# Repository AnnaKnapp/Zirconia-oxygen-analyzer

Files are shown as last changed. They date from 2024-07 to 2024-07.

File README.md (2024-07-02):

This repository contains the hardware design files and software for a high precision oxygen analyzer.

Analyzer hardware description:
The analyzer uses a fast-response dual-cell zirconia oxygen sensor manufactured by Process Sensing Technologies. A thermocouple probe is fitted into the sensor to enable a PID controller to hold the sensing element at a constant temperature. An analog feedback loop based on the one described by Benammar and Maskell (Benamar, 1993) holds the average O2 partial pressure inside the sealed central chamber of the sensor at a fixed ratio with that of the external sample gas. A 16-bit digital-to-analog-converter (DAC) is used to generate a 1 Hz sinusoidal waveform to pump oxygen into and out of the central chamber using the pumping cell. The digital pumping signal is controlled by a custom-built digital lock-in amplifier. The Nernst potential generated across the sensing cell is digitized with a 32-bit analog-to-digital converter. The amplitude and phase of the sense signal is calculated by the lock-in amplifier and a 10-second moving average filter is applied.

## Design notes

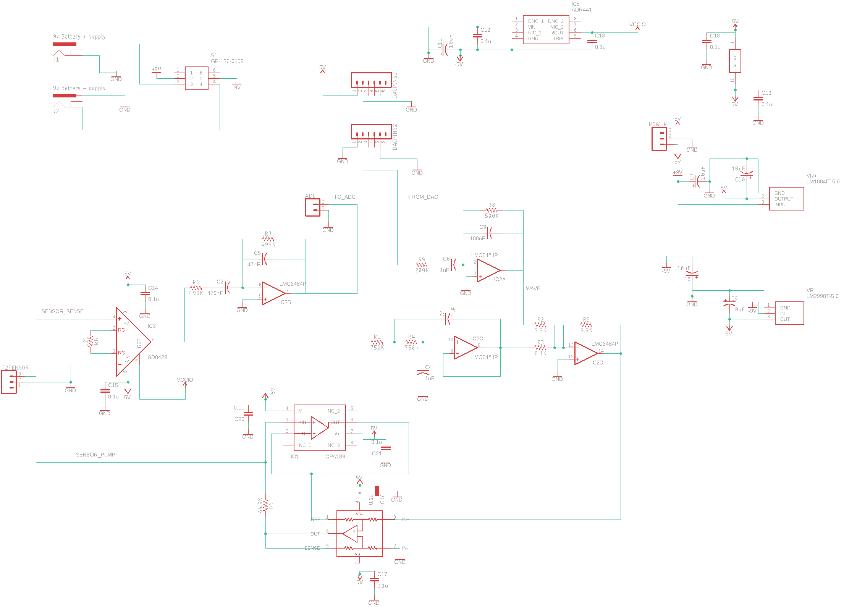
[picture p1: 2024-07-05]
Hardware/O2-analyzer-tracking-mode-schematic.png

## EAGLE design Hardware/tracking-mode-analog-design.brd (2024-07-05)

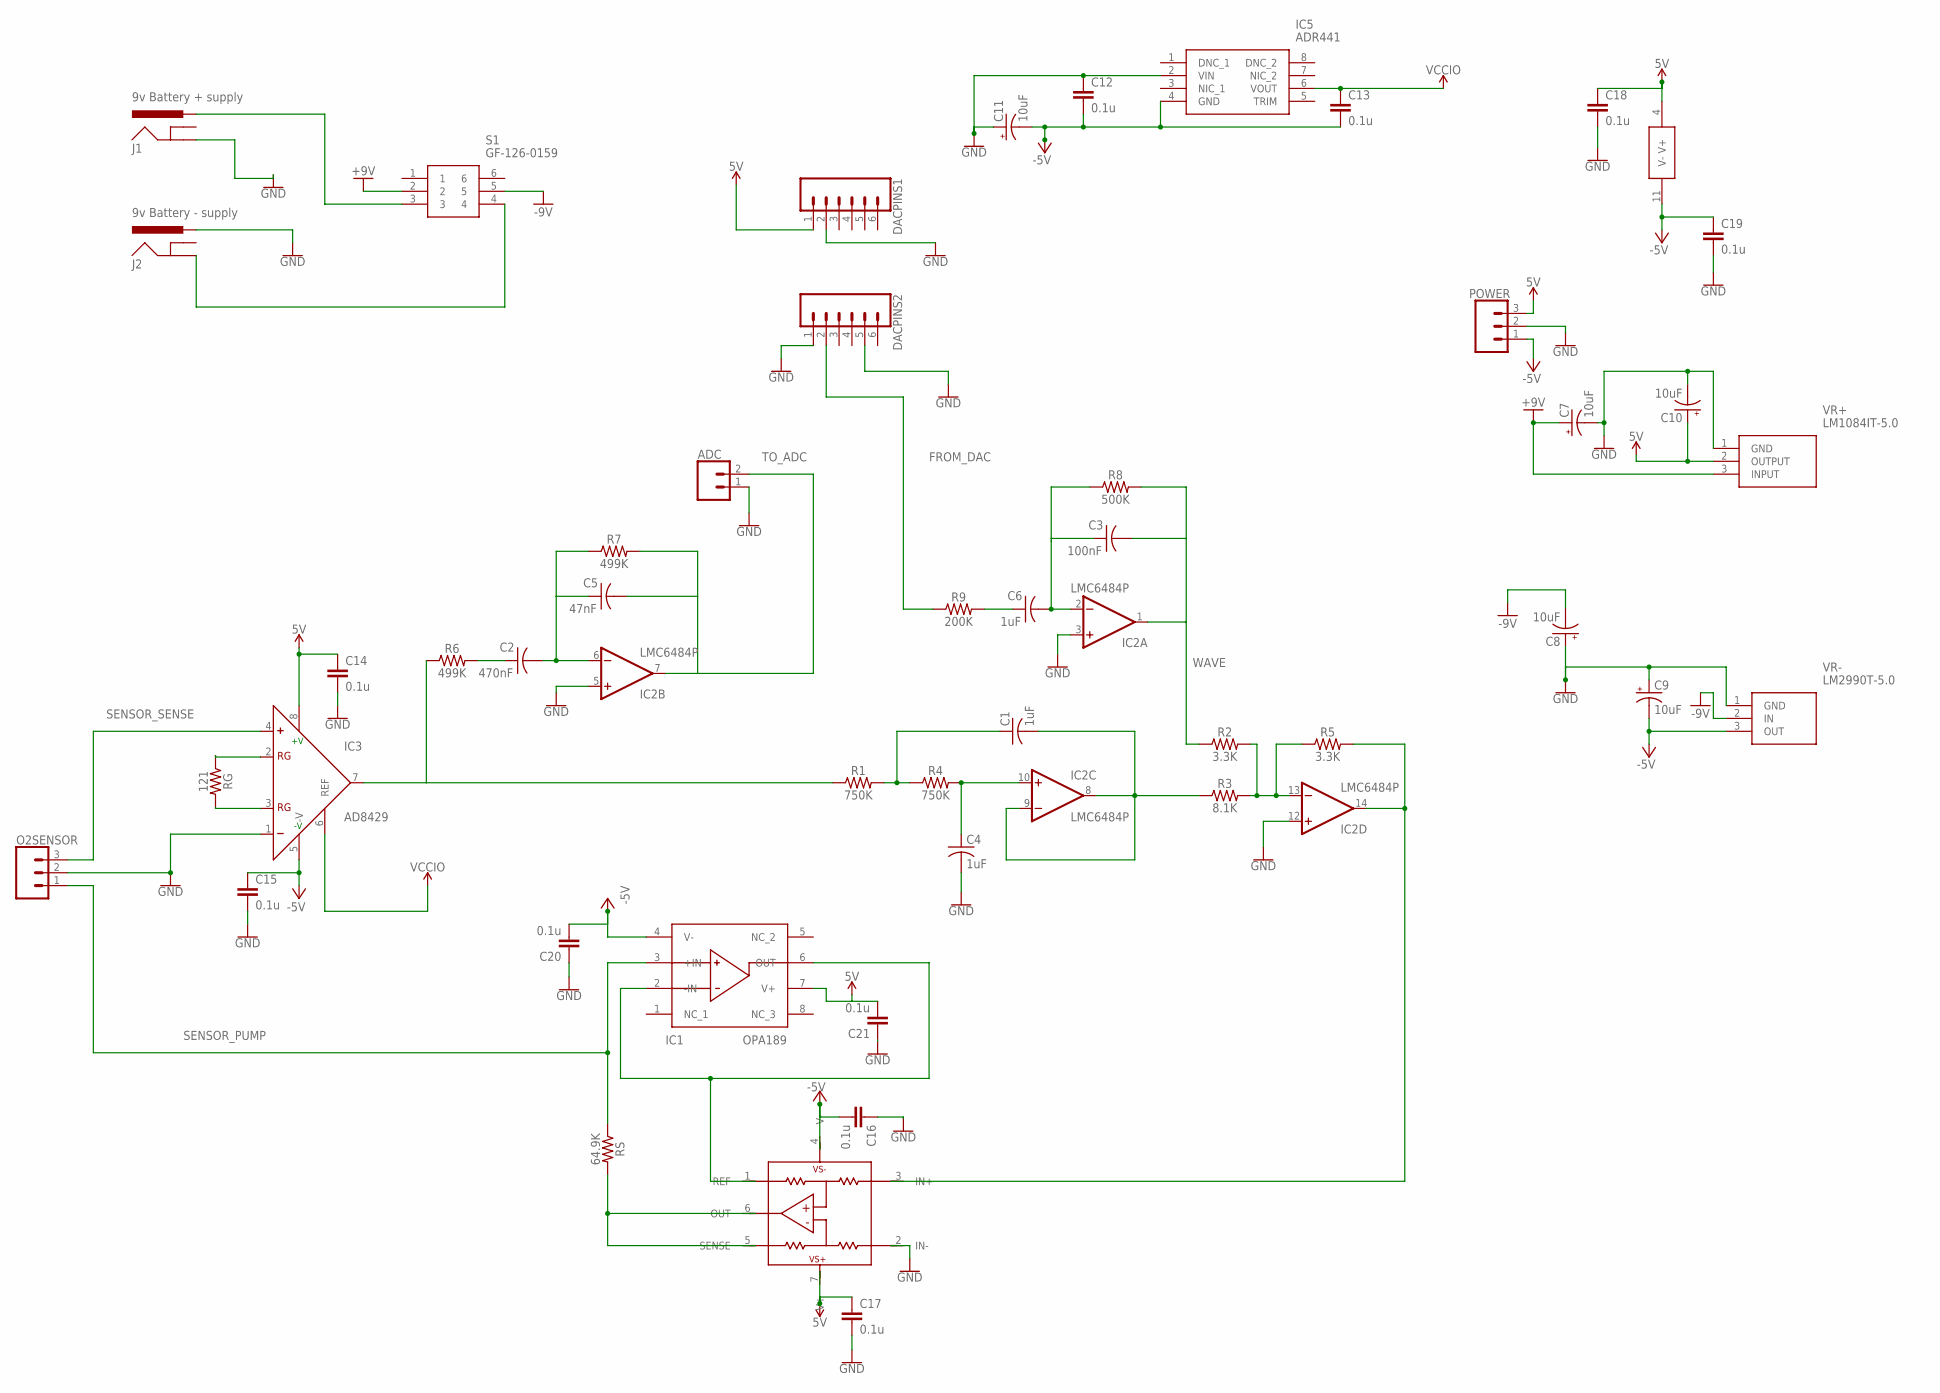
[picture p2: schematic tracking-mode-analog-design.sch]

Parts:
ADC: CONN_02; 1X02
C1, C4, C6: 1uF; C025-030X050
C2: 470nF; C025-030X050
C3: 100nF; C025-030X050
C5: 47nF; C025-030X050
C7, C8, C9, C10, C11: 10uF; CPOL-RADIAL-2.5MM-5MM-KIT
C12, C13, C14, C15, C16, C17, C18, C19, C20, C21: 0.1u; C025-040X050
DACPINS1, DACPINS2: CONN_06SILK_FEMALE_PTH; 1X06
IC1: OPA189; SOIC127P600X175-8N
IC2: LMC6484P; DIL14
IC3: AD8429; SO8
IC5: ADR441; SOIC127P600X175-8N
INA592: INA592; SO08
J1: 9v Battery + supply; POWER_JACK_PTH_BREAD
J2: 9v Battery - supply; POWER_JACK_PTH_BREAD
O2SENSOR: CONN_03; 1X03
POWER: CONN_03; 1X03
R1, R4: 750K; AXIAL-0.3
R2, R5: 3.3K; AXIAL-0.3
R3: 8.1K; AXIAL-0.3
R6, R7: 499K; AXIAL-0.3
R8: 500K; AXIAL-0.3
R9: 200K; AXIAL-0.3
RG: 121; AXIAL-0.3
RS: 64.9K; AXIAL-0.3
S1: GF-126-0159; GF1260159
VR+: LM1084IT-5.0; TO254P470X1028X1955-3P
VR-: LM2990T-5.0; TO254P470X1028X1955-3P

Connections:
5V: C10.1 (+), C14.1, C17.1, C18.1, C21.2, DACPINS1.1, IC1.7 (V+), IC2.4 (V+), IC3.8 (+V), INA592.7 (V+), POWER.3, VR+.2 (OUTPUT)
+V: C7.1 (+), S1.2, VR+.3 (INPUT)
-5V: C9.2 (-), C11.2 (-), C12.2, C13.2, C15.1, C16.2, C19.1, C20.2, IC1.4 (V-), IC2.11 (V-), IC3.5 (-V), IC5.4 (GND), INA592.4 (V-), POWER.1, VR-.3 (OUT)
-V: C8.2 (-), S1.5, VR-.2 (IN)
FROM_DAC: DACPINS2.2, R9.P$1 (1)
GND: ADC.1, C4.2, C7.2 (-), C8.1 (+), C9.1 (+), C10.2 (-), C11.1 (+), C12.1, C14.2, C15.2, C16.1, C17.2, C18.2, C19.2, C20.1, C21.1, DACPINS1.2, DACPINS2.1, DACPINS2.5, IC2.3 (+IN), IC2.5 (+IN), IC2.12 (+IN), IC3.1 (-), IC5.2 (VIN), INA592.2 (IN-), J1.GND, J2.PWR, O2SENSOR.2, POWER.2, VR+.1 (GND), VR-.1 (GND)
unnamed: C2.2, C5.1, IC2.6 (-IN), R7.P$1 (1)
unnamed: INA592.5 (SENSE), INA592.6 (OUT), RS.P$2 (2)
unnamed: C2.1, R6.P$2 (2)
unnamed: IC3.7 (OUT), R1.P$1 (1), R6.P$1 (1)
unnamed: C1.1, R1.P$2 (2), R4.P$1 (1)
unnamed: C4.1, IC2.10 (+IN), R4.P$2 (2)
unnamed: C1.2, IC2.8 (OUT), IC2.9 (-IN), R3.P$1 (1)
unnamed: IC2.13 (-IN), R2.P$2 (2), R3.P$2 (2), R5.P$1 (1)
unnamed: IC1.2 (-IN), IC1.6 (OUT), INA592.1 (REF)
unnamed: IC2.14 (OUT), INA592.3 (IN+), R5.P$2 (2)
unnamed: C6.1, R9.P$2 (2)
unnamed: IC3.2 (RG), RG.P$1 (1)
unnamed: C3.1, C6.2, IC2.2 (-IN), R8.P$1 (1)
unnamed: J2.GND, S1.4
unnamed: J1.PWR, S1.3
unnamed: IC3.3 (RG), RG.P$2 (2)
SENSOR_PUMP: IC1.3 (+IN), O2SENSOR.1, RS.P$1 (1)
SENSOR_SENSE: IC3.4 (+), O2SENSOR.3
TO_ADC: ADC.2, C5.2, IC2.7 (OUT), R7.P$2 (2)
VCCIO: C13.1, IC3.6 (REF), IC5.6 (VOUT)
WAVE: C3.2, IC2.1 (OUT), R2.P$1 (1), R8.P$2 (2)

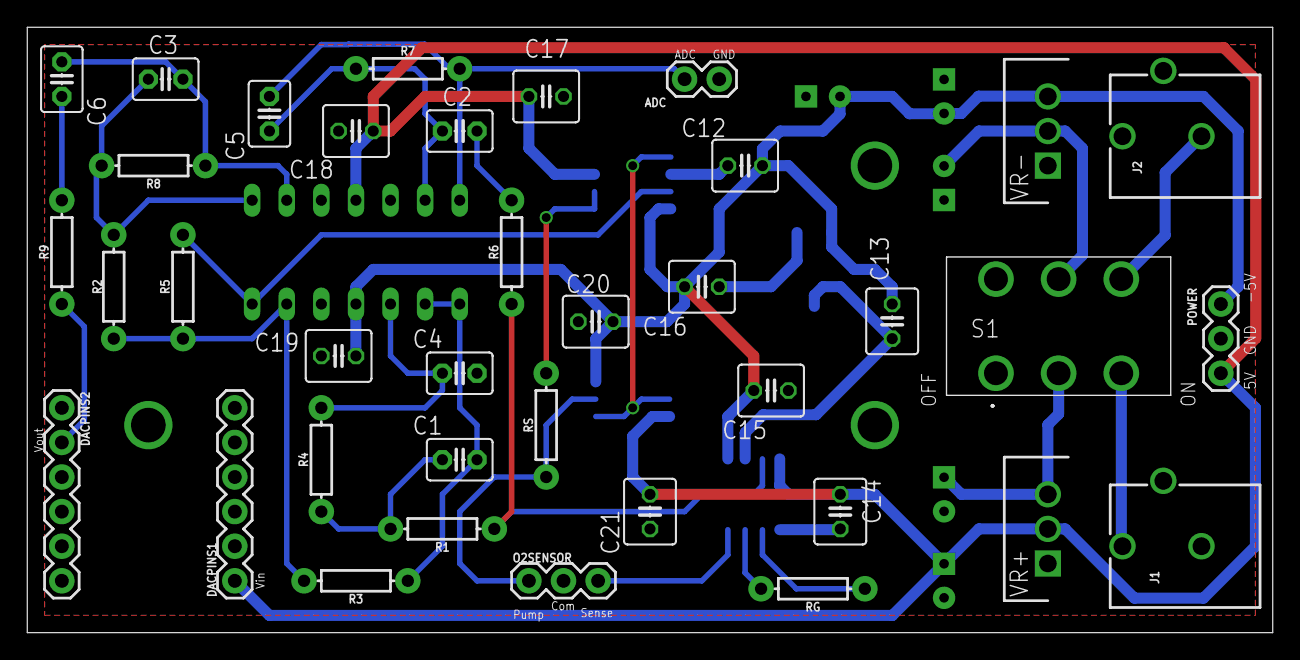
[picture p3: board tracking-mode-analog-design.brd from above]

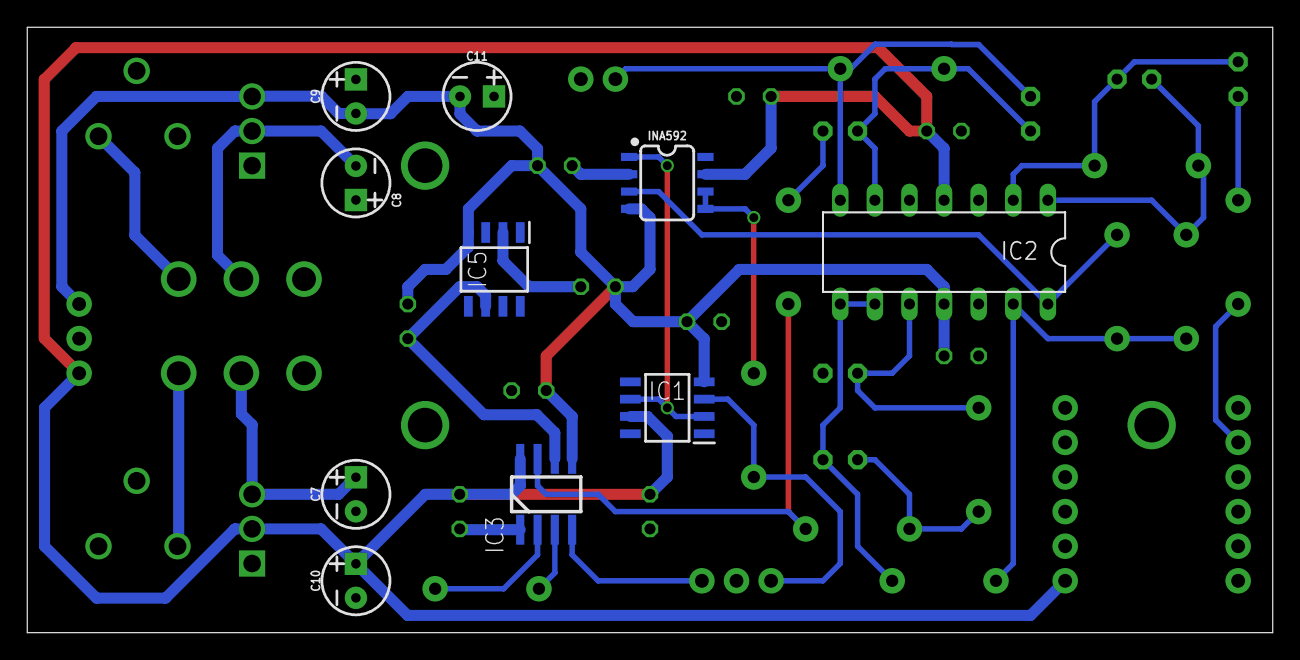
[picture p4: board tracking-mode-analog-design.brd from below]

Board: 2 copper layers, 91.4 x 44.5 mm, 47 parts (10 on the bottom side), 27 nets.

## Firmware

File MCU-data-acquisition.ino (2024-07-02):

// the ADC communicates using SPI, so include the library:
#include <SPI.h>
#include "Adafruit_AD569x.h"

#include <SPI.h>
#include "wiring_private.h" // pinPeripheral() function
//mosi on 16, miso on 7, sck on 17  

Adafruit_AD569x ad5693;
SPIClass mySPI (&sercom1, 7, 17, 16, SPI_PAD_0_SCK_1, SERCOM_RX_PAD_3);

const byte RREG = 0x20;     // ADS1262/3 read reg command
const byte WREG = 0x40;   // ADS1262/3 write reg command
const byte POWER_ADDRESS = 0x01;

const byte readcommand = 0x12;

// pins used for the connection with the sensor
// the other you need are controlled by the SPI library):
const int dataReadyPin = 3;
const int startpin = 4;
const int pwdnpin = 5;

const int dataReadyPin_2 = 26;
const int startpin_2 = 28;
const int pwdnpin_2 = 30;

byte dataToSend[8];

int i = 0;

// Generally, you should use "unsigned long" for variables that hold time
// The value will quickly become too large for an int to store
unsigned long previousMicros = 0;        // will store last time LED was updated

// constants won't change:
const long interval = 2000;
const int dac =  A0;
const PROGMEM unsigned int sine[] = {0x7F58,0x80EF,0x8286,0x841D,0x85B4,0x874A,0x88E1,
0x8A76,0x8C0C,0x8DA1,0x8F35,0x90C8,0x925B,0x93ED,
0x957F,0x970F,0x989F,0x9A2D,0x9BBA,0x9D47,0x9ED2,
0xA05B,0xA1E4,0xA36B,0xA4F0,0xA674,0xA7F7,0xA977,
0xAAF6,0xAC74,0xADEF,0xAF69,0xB0E1,0xB256,0xB3CA,
0xB53B,0xB6AB,0xB818,0xB982,0xBAEB,0xBC51,0xBDB4,
0xBF15,0xC074,0xC1D0,0xC329,0xC47F,0xC5D3,0xC724,
0xC871,0xC9BC,0xCB04,0xCC49,0xCD8B,0xCEC9,0xD005,
0xD13D,0xD271,0xD3A3,0xD4D1,0xD5FB,0xD722,0xD846,
0xD966,0xDA82,0xDB9B,0xDCAF,0xDDC0,0xDECE,0xDFD7,
0xE0DD,0xE1DE,0xE2DC,0xE3D5,0xE4CB,0xE5BC,0xE6A9,
0xE792,0xE877,0xE958,0xEA34,0xEB0C,0xEBE0,0xECAF,
0xED7A,0xEE40,0xEF02,0xEFC0,0xF078,0xF12D,0xF1DC,
0xF287,0xF32E,0xF3D0,0xF46D,0xF505,0xF598,0xF627,
0xF6B1,0xF736,0xF7B6,0xF832,0xF8A8,0xF91A,0xF986,
0xF9EE,0xFA51,0xFAAF,0xFB07,0xFB5B,0xFBAA,0xFBF4,
0xFC39,0xFC78,0xFCB3,0xFCE9,0xFD19,0xFD44,0xFD6B,
0xFD8C,0xFDA8,0xFDBF,0xFDD1,0xFDDE,0xFDE5,0xFDE8,
0xFDE5,0xFDDE,0xFDD1,0xFDBF,0xFDA8,0xFD8C,0xFD6B,
0xFD44,0xFD19,0xFCE9,0xFCB3,0xFC78,0xFC39,0xFBF4,
0xFBAA,0xFB5B,0xFB07,0xFAAF,0xFA51,0xF9EE,0xF986,
0xF91A,0xF8A8,0xF832,0xF7B6,0xF736,0xF6B1,0xF627,
0xF598,0xF505,0xF46D,0xF3D0,0xF32E,0xF287,0xF1DC,
0xF12D,0xF078,0xEFC0,0xEF02,0xEE40,0xED7A,0xECAF,
0xEBE0,0xEB0C,0xEA34,0xE958,0xE877,0xE792,0xE6A9,
0xE5BC,0xE4CB,0xE3D5,0xE2DC,0xE1DE,0xE0DD,0xDFD7,
0xDECE,0xDDC0,0xDCAF,0xDB9B,0xDA82,0xD966,0xD846,
0xD722,0xD5FB,0xD4D1,0xD3A3,0xD271,0xD13D,0xD005,
0xCEC9,0xCD8B,0xCC49,0xCB04,0xC9BC,0xC871,0xC724,
0xC5D3,0xC47F,0xC329,0xC1D0,0xC074,0xBF15,0xBDB4,
0xBC51,0xBAEB,0xB982,0xB818,0xB6AB,0xB53B,0xB3CA,
0xB256,0xB0E1,0xAF69,0xADEF,0xAC74,0xAAF6,0xA977,
0xA7F7,0xA674,0xA4F0,0xA36B,0xA1E4,0xA05B,0x9ED2,
0x9D47,0x9BBA,0x9A2D,0x989F,0x970F,0x957F,0x93ED,
0x925B,0x90C8,0x8F35,0x8DA1,0x8C0C,0x8A76,0x88E1,
0x874A,0x85B4,0x841D,0x8286,0x80EF,0x7F58,0x7DC1,
0x7C2A,0x7A93,0x78FC,0x7766,0x75CF,0x743A,0x72A4,
0x710F,0x6F7B,0x6DE8,0x6C55,0x6AC3,0x6931,0x67A1,
0x6611,0x6483,0x62F6,0x6169,0x5FDE,0x5E55,0x5CCC,
0x5B45,0x59C0,0x583C,0x56B9,0x5539,0x53BA,0x523C,
0x50C1,0x4F47,0x4DCF,0x4C5A,0x4AE6,0x4975,0x4805,
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


void setup() {
  Serial.begin(1000000);

  // start the SPI library:
  SPI.begin();
  SPI.setDataMode(SPI_MODE1);
  SPI.setClockDivider(SPI_CLOCK_DIV32);

  mySPI.begin();
  pinPeripheral(7, PIO_SERCOM);
  pinPeripheral(16, PIO_SERCOM);
  pinPeripheral(17, PIO_SERCOM);

  mySPI.setDataMode(SPI_MODE1);
  mySPI.setClockDivider(SPI_CLOCK_DIV32);


  if (ad5693.begin(0x4C, &Wire)) { // If A0 jumper is set high, use 0x4E
    Serial.println("AD5693 initialization successful!");
  } else {
    Serial.println("Failed to initialize AD5693. Please check your connections.");
    while (1) delay(10); // Halt
  }

  ad5693.reset();
  
  if (ad5693.setMode(NORMAL_MODE, true, false)) {
    Serial.println("AD5693 configured");
  } else {
    Serial.println("Failed to configure AD5693.");
    while (1) delay(10); // Halt
  }

  // initalize the  data ready and chip select pins:
  pinMode(dataReadyPin, INPUT_PULLUP);
  pinMode(startpin, OUTPUT);
  pinMode(pwdnpin, OUTPUT);

  pinMode(dataReadyPin_2, INPUT_PULLUP);
  pinMode(startpin_2, OUTPUT);
  pinMode(pwdnpin_2, OUTPUT);

  delay(3000);

  digitalWrite(pwdnpin, LOW);
  digitalWrite(pwdnpin_2, LOW);
  delay(500);
  digitalWrite(pwdnpin, HIGH);
  digitalWrite(pwdnpin_2, HIGH);
  digitalWrite(startpin, LOW);
  digitalWrite(startpin_2, LOW);
  delay(1000);
  Serial.println("writing");
               //pwr - vbias, int - chksum, mode0, mode1 - filt, mode2 -DR+PGA, inmux
  writeAdcFirst6Regs(0b00000011, 0b00000101, 0x00, 0b01100000, 0b00111100, 0b00001010);
               //pwr - vbias, int - chksum, mode0, mode1 - filt, mode2 -DR+PGA, inmux
  writeAdc_2_First6Regs(0b00000011, 0b00000101, 0x00, 0b01100000, 0b00001100, 0b00001010);
  delay(100);
  Serial.println("reading");
  readAdcFirst6Regs();
  readAdc_2_First6Regs();
  delay(100);
  digitalWrite(startpin, HIGH);
  digitalWrite(startpin_2, HIGH);
  delay(1000);
  
}


void loop() {
  unsigned long currentMicros = micros();
  if (currentMicros - previousMicros >= interval) {
    // save the last time
    previousMicros = currentMicros;
    
    // if the LED is off turn it on and vice-versa:
    //analogWrite(dac, sine[i]);
    ad5693.writeUpdateDAC(sine[i]);
    readBothADCsByCmdChk(i);
    i= i+1;
    if (i>499) {
      i=0;
    }
  }


}

void readADC1ByCmdChk(int index) {

  byte readcommand = 0x12;
  byte adcData[7] = {readcommand, 0x00, 0x00, 0x00, 0x00, 0x00, 0x00};
  SPI.transfer(adcData, 7); 
  //Serial.println(adcData[1]);
  //Serial.println(adcData[2]);
  //Serial.println(adcData[3]);
  //Serial.println(adcData[4]);
  //Serial.println(adcData[5]);
  //Serial.println(adcData[6]);
  //Serial.println((adcData[2]+adcData[3]+adcData[4]+adcData[5]+0x9B)&255);
  if (adcData[6] != ((adcData[2]+adcData[3]+adcData[4]+adcData[5]+0x9B)&255)) {
    Serial.println("checksum failed");
    } else {
      byte bigbyte = index >> 8;
      byte lilbyte = index;
      byte tosend[6] = {adcData[2], adcData[2], adcData[2], adcData[2], bigbyte, lilbyte};
      //long rawdata = (adcData[2])<<24 | int(adcData[3])<<16 | int(adcData[4])<<8 | int(adcData[5]);
      //Serial.println(rawdata);
      //float convFactor = 2.5/2147483648;
      //float convData = rawdata * convFactor;
      //byte * convBytes = (byte *) &convData;
      Serial.write(tosend, 6);
      //byte * idx = (byte *) &index;
      //Serial.write(idx, 2);
      //Serial.println(convData);
      }
  }


void readBothADCsByCmdChk(int index) {
  byte adc1Data[7] = {readcommand, 0x00, 0x00, 0x00, 0x00, 0x00, 0x00};
  SPI.transfer(adc1Data, 7);
  byte adc2Data[7] = {readcommand, 0x00, 0x00, 0x00, 0x00, 0x00, 0x00};
  mySPI.transfer(adc2Data, 7);
  //Serial.println(adcData[1]);
  //Serial.println(adcData[2]);
  //Serial.println(adcData[3]);
  //Serial.println(adcData[4]);
  //Serial.println(adcData[5]);
  //Serial.println(adcData[6]);
  //Serial.println((adcData[2]+adcData[3]+adcData[4]+adcData[5]+0x9B)&255);
  if (adc1Data[6] != ((adc1Data[2]+adc1Data[3]+adc1Data[4]+adc1Data[5]+0x9B)&255) & adc2Data[6] != ((adc2Data[2]+adc2Data[3]+adc2Data[4]+adc2Data[5]+0x9B)&255)) {
    Serial.println("checksum failed");
    } else {
      byte bigbyte = index >> 8;
      byte lilbyte = index;
      byte tosend[10] = {adc1Data[2], adc1Data[3], adc1Data[4], adc1Data[5], adc2Data[2], adc2Data[3], adc2Data[4], adc2Data[5], bigbyte, lilbyte};
      //long rawdata = (adcData[2])<<24 | int(adcData[3])<<16 | int(adcData[4])<<8 | int(adcData[5]);
      //Serial.println(rawdata);
      //float convFactor = 2.5/2147483648;
      //float convData = rawdata * convFactor;
      //byte * convBytes = (byte *) &convData;
      Serial.write(tosend, 10);
      //byte * idx = (byte *) &index;
      //Serial.write(idx, 2);
      //Serial.println(convData);
      }
  }


void writeAdc_2_First6Regs(byte power, byte interface, byte mode0, byte mode1, byte mode2, byte inpmux) {

  byte opcode = WREG | POWER_ADDRESS;
  byte numberToSend = 0x05;
  byte dataToSend[8] = {opcode, numberToSend, power, interface, mode0, mode1, mode2, inpmux};

  mySPI.transfer(dataToSend, 8); //Send register location
}

void writeAdcFirst6Regs(byte power, byte interface, byte mode0, byte mode1, byte mode2, byte inpmux) {

  byte opcode = WREG | POWER_ADDRESS;
  byte numberToSend = 0x05;
  byte dataToSend[8] = {opcode, numberToSend, power, interface, mode0, mode1, mode2, inpmux};

  SPI.transfer(dataToSend, 8); //Send register location
}


void readAdc_2_First6Regs() {

  byte opcode = RREG | POWER_ADDRESS;
  byte numberToSend = 0x05;
  byte dataToSend[8] = {opcode, numberToSend, 0x00, 0x00, 0x00, 0x00, 0x00, 0x00};

  mySPI.transfer(dataToSend, 8); //Send register location
  Serial.println(dataToSend[2]);
  Serial.println(dataToSend[3]);
  Serial.println(dataToSend[4]);
  Serial.println(dataToSend[5]);
  Serial.println(dataToSend[6]);
  Serial.println(dataToSend[7]);
}

void readAdcFirst6Regs() {

  byte opcode = RREG | POWER_ADDRESS;
  byte numberToSend = 0x05;
  byte dataToSend[8] = {opcode, numberToSend, 0x00, 0x00, 0x00, 0x00, 0x00, 0x00};

  SPI.transfer(dataToSend, 8); //Send register location
  Serial.println(dataToSend[2]);
  Serial.println(dataToSend[3]);
  Serial.println(dataToSend[4]);
  Serial.println(dataToSend[5]);
  Serial.println(dataToSend[6]);
  Serial.println(dataToSend[7]);
}

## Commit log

2024-07-02 Added arduino code for MCU
2024-07-05 added eagle files for schematic and board
    [tracking-mode-analog-design.brd, tracking-mode-analog-design.sch]

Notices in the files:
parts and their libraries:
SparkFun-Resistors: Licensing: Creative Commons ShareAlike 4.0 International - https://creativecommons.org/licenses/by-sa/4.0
